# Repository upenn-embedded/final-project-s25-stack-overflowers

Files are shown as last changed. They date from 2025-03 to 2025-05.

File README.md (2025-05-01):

Review Assignment Due Date (https://classroom.github.com/a/WXeqVgks)

# final-project-skeleton

* Team Number: 14
* Team Name: Stack Overflowers
* Team Members: Sofia Hedlund and Amanda Tapia Garbelloto
* GitHub Repository URL: https://github.com/upenn-embedded/final-project-s25-stack-overflowers.git
* GitHub Pages Website URL: [for final submission]

## Final Project Proposal

### 1. Abstract

*In a few sentences, describe your final project.*

We want to make a braille printer that the user can input text into with a keyboard and have it print out the text into readable braille bumps. We plan to do this by 3D printing braille letters onto a stamp that will then rotated according to the text input and stamped down onto the paper with a motor. This project will use power management, interrupts for reading from the keyboard, and timers to control the stepper motor.

### 2. Motivation

*What is the problem that you are trying to solve? Why is this project interesting? What is the intended purpose?*

The project aims to enhance accessibility for people with reduced vision. By automatically transforming text into braille, people who can't see text are able to expand their integration to reading materials by possessing a personal device that can make any text available for them without requiring extra translators or specialized equipment.

### 3. System Block Diagram

*Show your high level design, as done in WS1 and WS2. What are the critical components in your system? How do they communicate (I2C?, interrupts, ADC, etc.)? What power regulation do you need?*
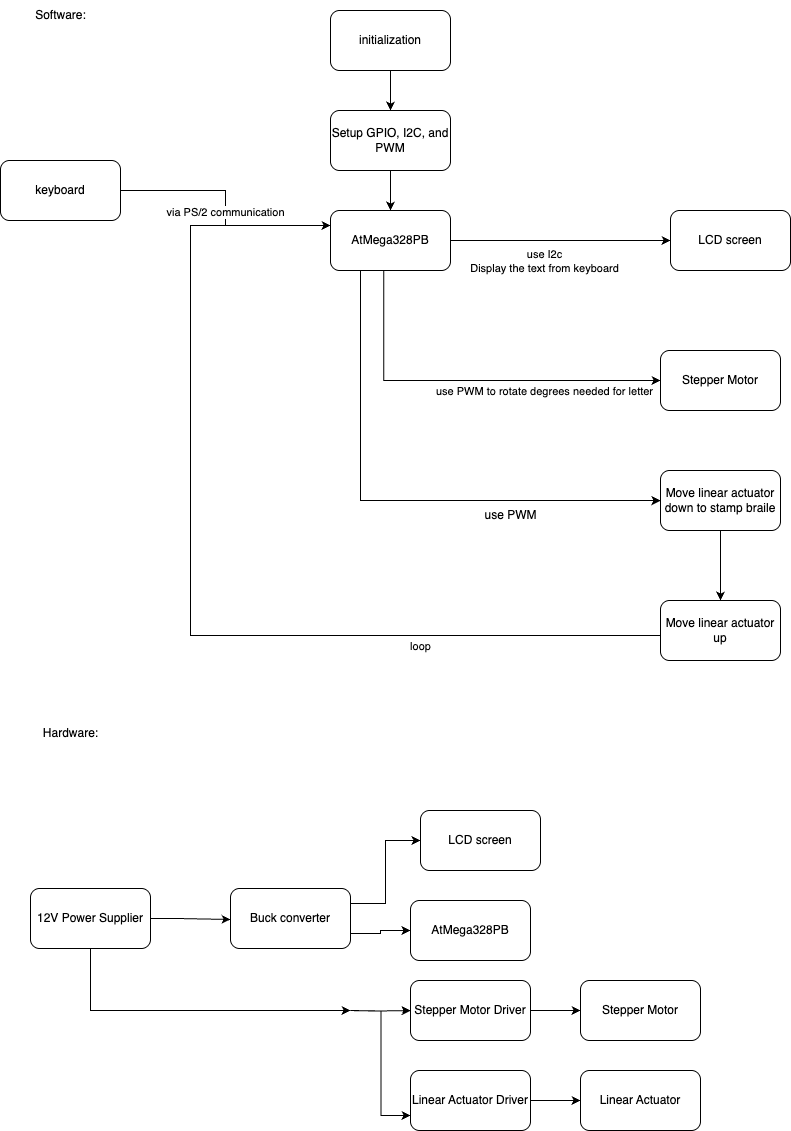
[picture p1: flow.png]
flow


### 4. Design Sketches

*What will your project look like? Do you have any critical design features? Will you need any special manufacturing techniques to achieve your vision, like power tools, laser cutting, or 3D printing?*
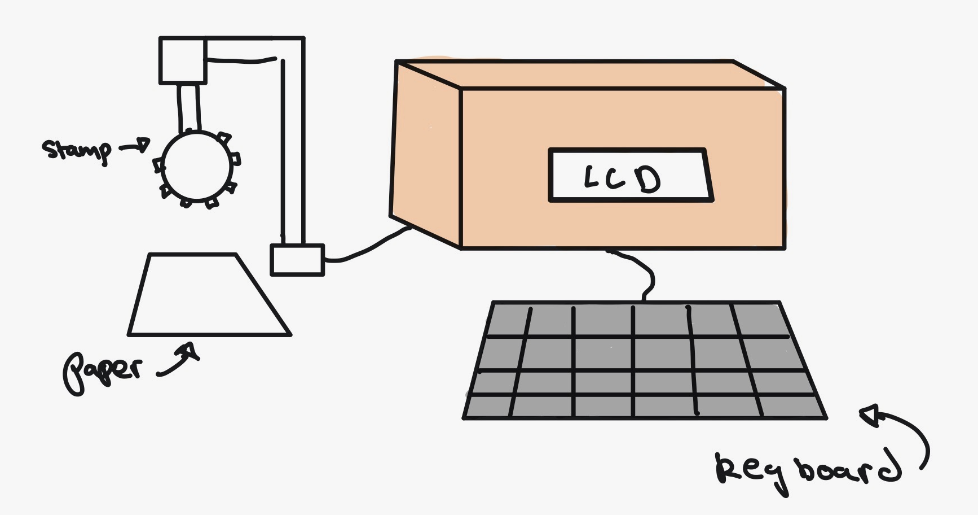
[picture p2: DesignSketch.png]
DesignSketch


We will need to 3D print the braille stamp to attach to the motor and also need some kind of container to hold the LCD and the wiring needed to power the system. We will also have to 3D print a stand to hold the linear actuator.

### 5. Software Requirements Specification (SRS)

*Formulate key software requirements here. Think deeply on the design: What must your device do? How will you measure this during validation testing? Create 4 to 8 critical system requirements.*

*These must be testable! See the Final Project Manual Appendix for details. Refer to the table below; replace these examples with your own.*

**5.1 Definitions, Abbreviations**

Here, you will define any special terms, acronyms, or abbreviations you plan to use for hardware

PWM- Pulse Width Modulation

ASCII- American Standard Code for Information Exchange

LCD- Liquid Crystal Display

**5.2 Functionality**

| ID     | Description                                                                                                                                                                                                                                                                               |
| ------ | ----------------------------------------------------------------------------------------------------------------------------------------------------------------------------------------------------------------------------------------------------------------------------------------- |
| SRS-01 | The microcontroller will process each letter of the text input and connect it to its corresponding braille. We can test its accuracy by plugging in sample characters and evaluating the different outputs of the MCU.                                                                    |
| SRS-02 | The system will translate each recognized letter into a PWM signals sending specific rotation angle for the Braille stamp mechanism, ensuring accurate letter selection. In this phase, we can actually measure the rotation angle for each character once we have our stamper connected. |
| SRS-03 | The stamping should be precisely timed, ensuring that the stepper motor finishes its rotation completely before the stamp is pressed again to prevent misalignment.                                                                                                                       |
| SRS-04 | The linear actuator will move the stamping mechanism, positioning the stamp at the correct location on the paper. The actuator should only move the stamp after it is pressed.                                                                                                            |
| SRS-05 | The software will have debouncing to filter out noise from the keyboard.                                                                                                                                                                                                                  |

### 6. Hardware Requirements Specification (HRS)

*Formulate key hardware requirements here. Think deeply on the design: What must your device do? How will you measure this during validation testing? Create 4 to 8 critical system requirements.*

*These must be testable! See the Final Project Manual Appendix for details. Refer to the table below; replace these examples with your own.*

**6.1 Definitions, Abbreviations**

Here, you will define any special terms, acronyms, or abbreviations you plan to use for hardware

Stepper Motor- DC motor that has very precise conotrol that will help us avoid error when rotating the stamp to the position of the letter.

Linear Actuator- Moves in a straight line so that we can move the stamp up and down.

**6.2 Functionality**

| ID     | Description                                                                                                                                                                                                                                                                       |
| ------ | --------------------------------------------------------------------------------------------------------------------------------------------------------------------------------------------------------------------------------------------------------------------------------- |
| HRS-01 | The device will require a keyboard module for text entry, this will communicate with the ATmega238 via PS/2.                                                                                                                                                                      |
| HRS-02 | It will also display the typed text to a LCD screen (I2C interface) to provide user feedback before printing. We will test the keyboard and the screen by seeing whether the later is displaying the correct keyboard inputs in real time.                                        |
| HRS-03 | The MCU will generate a PWM signal to control a stepper motor, which will rotate the Braille stamp mechanism to the correct character position. While working on this part we will ensure that the PWM signals are accurately rotating the stamp with a negligible error accuracy |
| HRS-04 | A linear actuator will move the stamp up and down to imprint the letters on to the paper A motor driver will be used to control the linear actuator, ensuring reliable movement without overloading the MCU.                                                                      |
| HRS-05 | The power system will need 12V power source and a buck converter for 5V to power the MCU, LCD, Stepper, and Linear Actuator.                                                                                                                                                      |

### 6. Bill of Materials (BOM)

*What major components do you need and why? Try to be as specific as possible. Your Hardware & Software Requirements Specifications should inform your component choices.*

*In addition to this written response, copy the Final Project BOM Google Sheet and fill it out with your critical components (think: processors, sensors, actuators). Include the link to your BOM in this section.*

The major components that we need are a stepper motor/driver to spin the braille stamp and a linear actuator/driver to move the stamp up and down. We chose our stepper motor in order have a lot precision over the amount of degrees the motor turns, so that the correct braille letter is stamped. We also chose for it to be 12V in order to ensure that it will have enough torque required to spin the braille stamp accurately. The driver will let us send simple STEP and DIR signals to control the stepper which will help us easily control the stepper. We chose a linear actuator to stamp down and a H-bridge so that we can move the actuator both up and down. Our budget was a main factor in choosing our linear actuator, because a lot of them were quite pricey (around 70$), so we chose the most affordable option we could find that fit with our system. We chose our keboard to be able to communicate over PS/2 because it is simpler to work with then USB communication which would likely need outside libraries. We will also use the LCD screen from Lab 4 and use the ATmega328Pb Xplained mini board.

[BOM](https://docs.google.com/spreadsheets/d/10AtQ8pPZeS8G-I5d4TY12WMqAhfvfrOR0J54DZgVhsI/edit?usp=sharing)

### 8. Final Demo Goals

*How will you demonstrate your device on demo day? Will it be strapped to a person, mounted on a bicycle, require outdoor space? Think of any physical, temporal, and other constraints that could affect your planning.*

We will demonstrate our device on demo day by entering in text to the keyboard, which will then be displayed on the LCD and then printed in braille by the stepper motor which will rotate to position the correct letter and the linear actuator which will stamp it down. Some physical constraints are that we need to have enough table space for the keyboard, LCD container, stepper motor, and paper. Because we are stamping the text out letter-by-letter, printing out a word or a short phrase will be more realistic to demonstrate out project without excessive time delay. At the end of the demo, the user can feel the braille stamped out on the paper, and can also compare it against the text on the LCD.

### 9. Sprint Planning

*You've got limited time to get this project done! How will you plan your sprint milestones? How will you distribute the work within your team? Review the schedule in the final project manual for exact dates.*

| Milestone  | Functionality Achieved                                                                                                                                    | Distribution of Work                                         |
| ---------- | --------------------------------------------------------------------------------------------------------------------------------------------------------- | ------------------------------------------------------------ |
| Sprint #1  | -3D print braille stamp<br />-Create rotating code for the stamp that maps characters to braille positions                                               | 3D printing- Amanda<br />Code- Sofia                         |
| Sprint #2  | -Add keyboard/LCD screen that displays the input text<br />-3D print stand for the linear actuator and stepper<br />-Debug rotation issues with the stamp | Keyboard/LCD- Sofia<br />3D print- Amanda <br />Debug- both |
| MVP Demo   | -Create code to move linear actuator up and down<br />-Debug movement with linear actuator                                                                | Code/movement- both                                          |
| Final Demo | -Refine precision of the motor movements                                                                                                                 | Both                                                         |

## Sprint Review #1

### Last week's progress

During this sprint, we finished the code to connect the serial terminal to the LCD screen so that it displays the text the user inputs. We also implemented the logic behind mapping the characters to their braille representations in binary, and the code to turn the pins the solenoids will be attached on to HIGH. We also started CAD for the structure that will hold the solenoids above the paper. We have committed the code for this part on github.

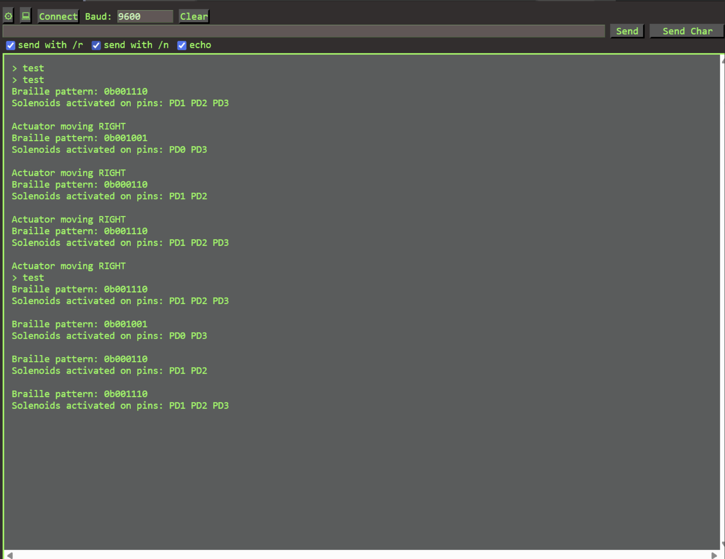
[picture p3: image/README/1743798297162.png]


### Current state of project

After the project presentation we got some feedback from the class on how to improve the stamping mechanism, so instead of using a wheel we will be working with six solenoids to support the full braille pattern.

We also took the professor's advice and are using our serial terminal to type out what we want to be translated to braille, instead of connecting another keyboard.

So, for each letter typed into the terminal, we have built the code that is recognizing them and translating it to the braille pattern, relating each dot to its correspondent solenoid and activating them. Since our parts have not arrived we still haven't tested their functionality, but so far our printed results seem to be in order. We have also wired the LCD screen and tested that it correctly displays what is being typed.

We have now ordered all the hardware parts needed for the project, but they haven't been delivered yet, so we are hoping to have them by next week so that we can also put them together with the stands we are designing and 3D printing. We have started working on the CAD structures for our supports and are planning on printing them this next week.

### Next week's plans

Next week we are going to be working on the hardware and testing the actual implementation of our code to the devices as soon as they arrive. So far we have the code for the solenoids push and pull, however since they were ordered later, we are probably going to implement first the movement of the linear actuator, which should follow the x-axis from right to left (since we are going to be stamping upside down).  Sofia will be working on combining the software and the hardware and debugging any issues that come up which will take around 5 hours, and will be considered “done” once the solenoids correctly move up and down with the character inputs and the linear actuator is able to move corresponding to each character.

We are also going to use the 3D printers to build the support for the solenoids and the box to keep most of our hardware connections, including the breadboards and ATmega238. Amanda will be working on 3D printing these supports with SolidWorks, which we are estimating will take around 5 hours and will be considered “done” once we send off the print request.

## Sprint Review #2

### Last week's progress

The solenoids that we ordered came, so we wired them with diodes and transistors and connected them to our MCU. From there, we debugged some issues with them correctly moving in and out, and realized two out of the six solenoids didn’t work properly, so we will be reordering them. We also completed and submitted CAD designs for a structure to hold the linear actuator and breadboard and also a structure to hold the actual solenoids.  We put the CAD files and a[ video](https://drive.google.com/file/d/1jELO6MgL8OEqHJt7nowW01g8Ehbm2qYE/view?usp=sharing) of the solenoids working with text input in the repo.

### Current state of project

At this point, we can see the braille patterns pretty accurately and have the LCD display our words at the same time as each letter is translated. We have wired part of the hardware and now need to add the linear actuator so that the motor moves on the x-axis as it prints on paper. We are waiting for the 3D printer to assemble all pieces and verify that they are the expected and can support our hardware accordingly.

### Next week's plan

Next week, we hope to figure out a way to attach a structure onto the tops of the solenoids so that when they move up and down they will stamp braille in the correct standardized dimensions. We also hope to get the linear actuator to work and move correctly as letters are stamped down. If the 3D print jobs are completed, we will also work on assembling the parts together.

We are planning on working together on most goals for next week, getting the linear actuator to work and debug any problems we might find with it should take around 4 hours to get the motor working and 3-5 hours for an attachment to the solenoids depending on how we implement it. Assembling the 3D pieces together should be pretty straightforward, but if we need to fix something or maybe redesign it, it might take up to 3 hours.

If everything works correctly, we also want to implement a feature connecting the braille machine to the blynk app, using the ESP32 interface so that we could try typing in our phones and getting the physical braille output.

## MVP Demo

1. Show a system block diagram & explain the hardware implementation.

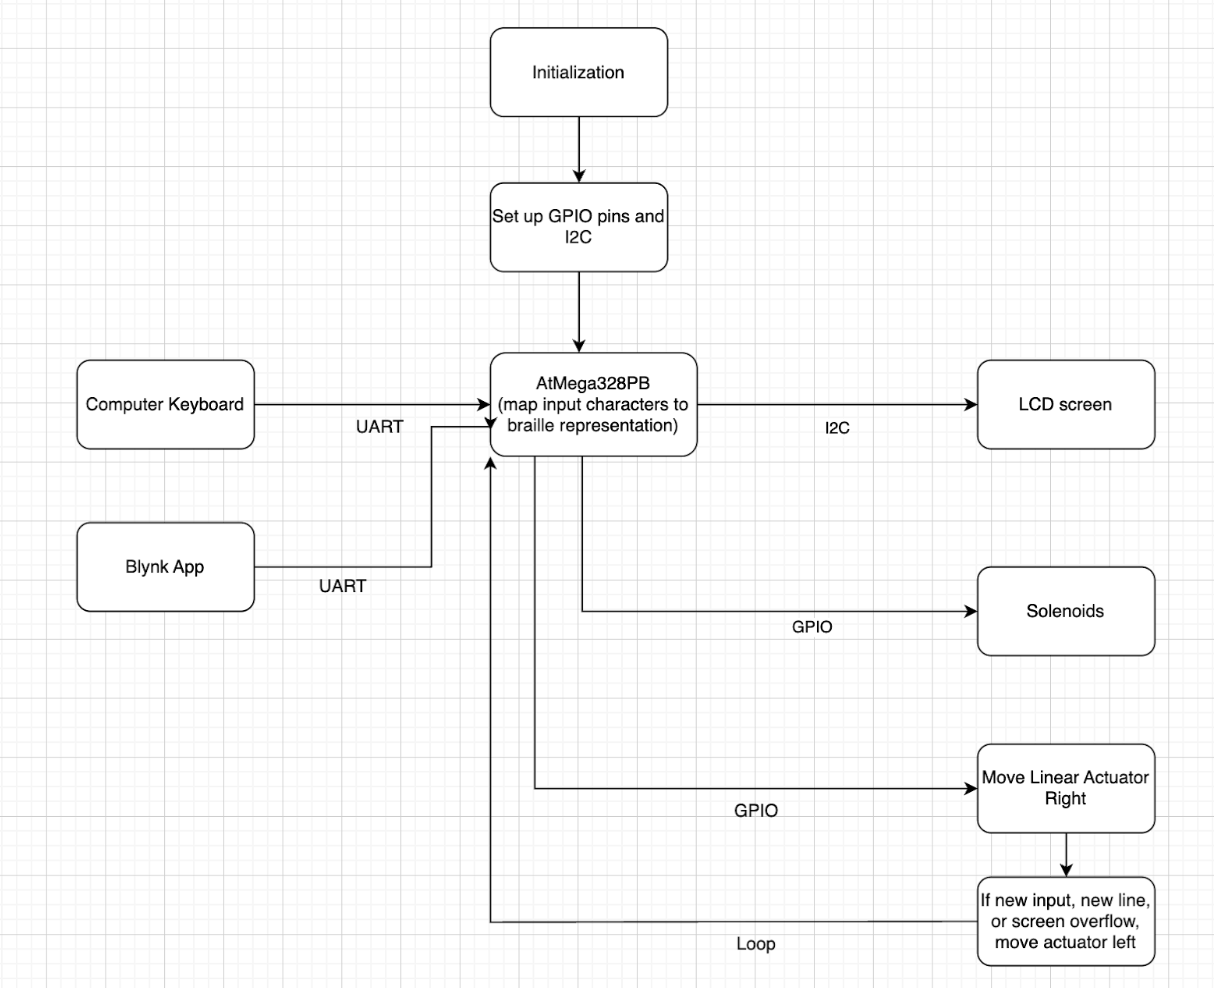
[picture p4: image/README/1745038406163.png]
   
2. Explain your firmware implementation, including application logic and critical drivers you've written.

   Our firmware currently takes in input using UART from the computer keyboard and converts it to bit representations of the Braille patterns. With these, it moves the solenoids up and down and the linear actuator right and left in order to create printed Braille. Using the UART driver, we store string inputs in a buffer and then process the string character-by-character by looking up the corresponding 6-bit Braille pattern from our table. In the bit representation, it will be a 1 if there is a bump and a 0 if there is no bump for each of the six Braille cells. These bits are then mapped to the six GPIO pins on our AtMega that control the solenoids in the activate_solenoids() function which sets and clears these pins with delays for stamping. We also have the functions actuator_move_out() and actuator_move_in() that control the GPIO pins to control the actuator for each character stamped out. The actuator moves out in between each character, and then will reset to the beginning of the line (moving in) for any new input, line overflow, or screen overflow. We also update an LCD screen in real-time as each character is stamped out so the user knows what is being written.
3. Demo your device.

   [https://drive.google.com/file/d/1WyQ7toSs-Gw57tEabU6b0ifRRfPq295w/view?usp=drivesdk](https://drive.google.com/file/d/1WyQ7toSs-Gw57tEabU6b0ifRRfPq295w/view?usp=drivesdk)

   [https://drive.google.com/file/d/1pV1rKBUoVU073-nwK2HYLF4Z8lEnAvDB/view?usp=drivesdk](https://drive.google.com/file/d/1pV1rKBUoVU073-nwK2HYLF4Z8lEnAvDB/view?usp=drivesdk)
4. Have you achieved some or all of your Software Requirements Specification (SRS)?

   1. Show how you collected data and the outcomes.
   2. We are using the LCD screen, which communicates over SPI, in order to display our typed inputs into the serial terminal. The screen shows our written words correctly and the linear actuator moves forth with each character and back at every new line to start typing the next input.
   3. Our motor and solenoids are also driven by GPIO. We changed our initial implementation, so we no longer needed to use PWM signals in order to rotate a stepper motor and instead are using GPIO to set the solenoids high or low according to our pattern.
   4. The timing precision of the machine has also been working reasonably well. We move the linear actuator after stamping each letter and then activate the solenoids. When a new input is written, representing a new line on the LCD, the actuator moves fully back and restart by the beginning of the line. We can still try to work on the precision of the movements, changing delays for example, but overall our system is working as expected.
5. Have you achieved some or all of your Hardware Requirements Specification (HRS)?

   1. Show how you collected data and the outcomes.
   2. We changed the interface of our input communicating tot he ATMega, so instead of a separate keyboard we are using the serial terminal connection (UART) from our laptops to the MCU and LCD display, which has been working accordinly.
   3. Our linear actuator and solenoids (stamping machine itself) are moving as expected. The linear actuator moves in the x-axis at every character and the solenoids are activated when it is no longer moving.
   4. We are using two different power sources. The Linear Actuator and the solenoids need 12V, so we ordered a battery to provide enough voltage and since the actuator also draws significant current (5A) we looked for a 12V battery with 7A current to support the actuator plus the six solenoids.
6. Show off the remaining elements that will make your project whole: mechanical casework, supporting graphical user interface (GUI), web portal, etc.

   We are still waiting to get our mechanical support for the linear actuator from the 3D printer. This element will be the overall case for the entire system and will provide a place to place the ATmega238 along with the breadboards. Internaly the box will also have a shelf to support the linear actuator, with a hole to the side were the moving part of our actuator will come out and move along the paper. This part of the linear actuator will also be propoerly connected to a solenoid support, where our six solenoids will be held in the right braille position and the bottom of each solenoid will be attached to a spike to poke the braille with correct pattern.

   In the firmware we will also finish implementing the connection between the feather and the serial terminal through UART so that we can use our phones to type our inputs. We will also work on debugging the current code and correcting any errors or delays which might be causing some unsynchronized movement between the solenoids and the actuator.

   We are still need to create a web portal for the project and add its link to our repo.
7. What is the riskiest part remaining of your project?

   The riskiest remaining part of our project is attaching parts to the tops of the solenoids so that we are able to print braille in the correct standard size/format. Because the solenoids are bulky currently, we need to design and apply attachments to each solenoid that will allow them to stamp in the braille with correct spacing to be readable.
   We also looked up the standard size of braille and are thinking of scaling it by 2 for making the stamp more visible and easier to manage due to our solenoid size and distance.

   1. How do you plan to de-risk this?

      We plan to de-risk this by properly trying out different materials that we can use to stamp down, such as 3D printing or rubber tips, and we will try attaching them in multiple ways to make sure that they are stable. We will also test out our braille stamp options on the braille paper, and adjust the stamping pressure with the solenoids depending on the results.
8. What questions or help do you need from the teaching team?

   We mostly need to continue debugging the motion of the linear actuator and finish assembling it with the 3D printed parts. We also hope to integrate it with the feather and the Blynk app which we could need some support with.

   From our last try, we were able get the inputs from the Blynk app to the serial terminal of the arduino, however, we still can't transmit the strings through UART to the LCD, so we will most likely go to office hours this week to finish this implementation.

## Final Project Report

Don't forget to make the GitHub pages public website!
If you’ve never made a GitHub pages website before, you can follow this webpage (though, substitute your final project repository for the GitHub username one in the quickstart guide):  [https://docs.github.com/en/pages/quickstart](https://docs.github.com/en/pages/quickstart)

### 1. Video

Here is a [link](https://drive.google.com/file/d/1xeawdyDZGxui-g1Ykbre4UoAcS7RQmn_/view?usp=sharing) to our final project! :)

### 2. Images

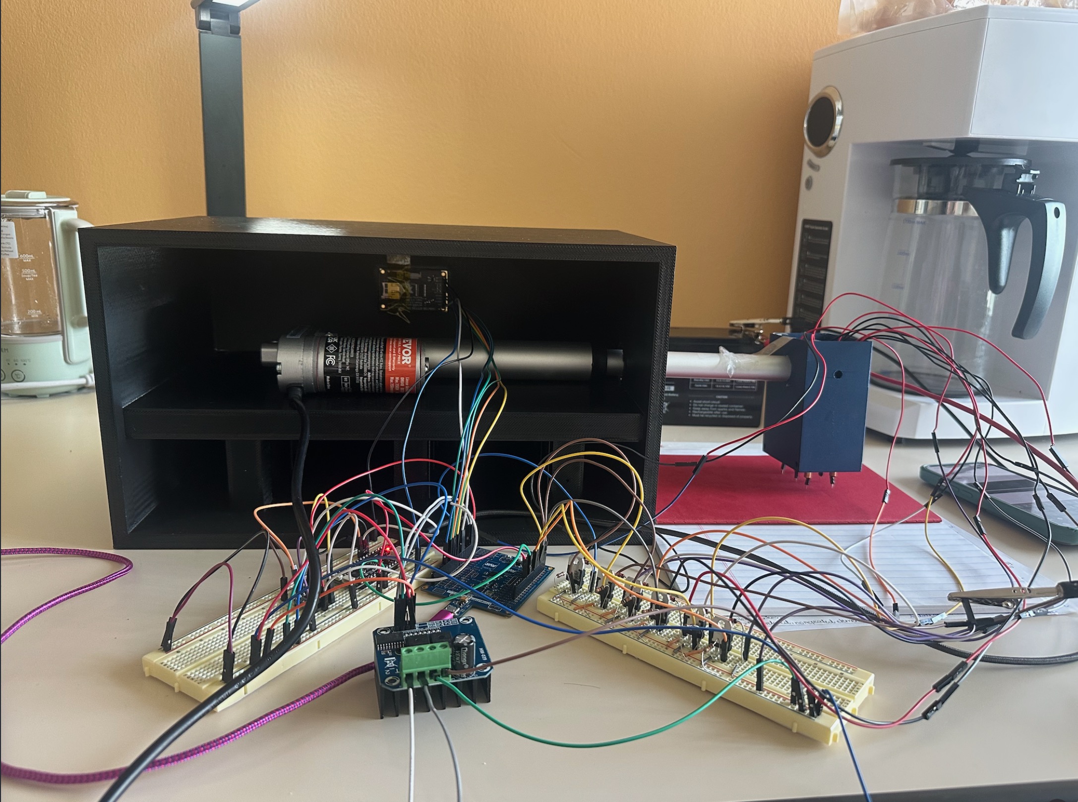
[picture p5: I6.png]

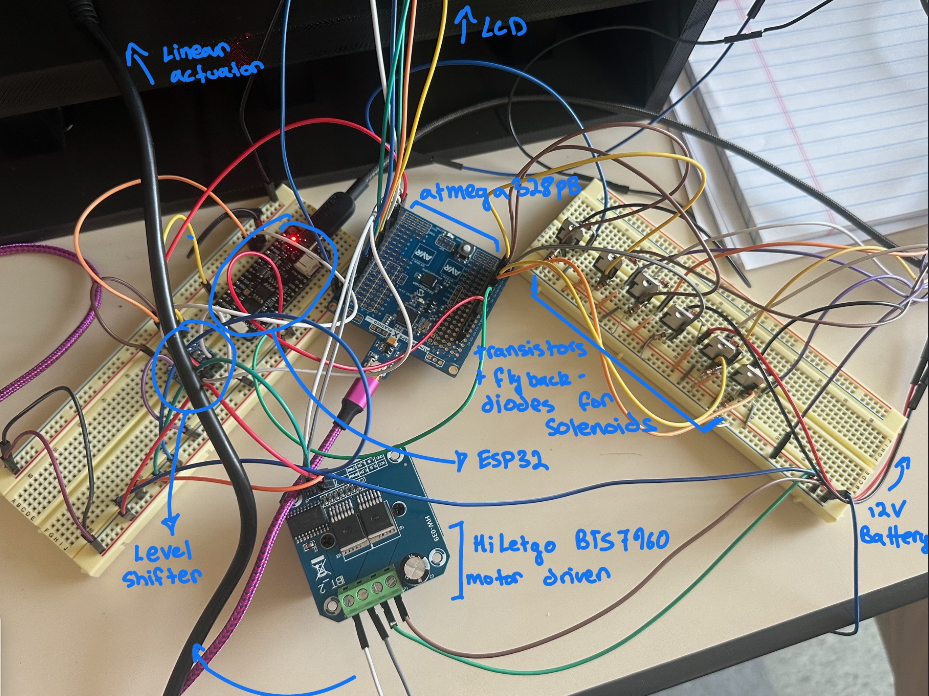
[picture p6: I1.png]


<p>
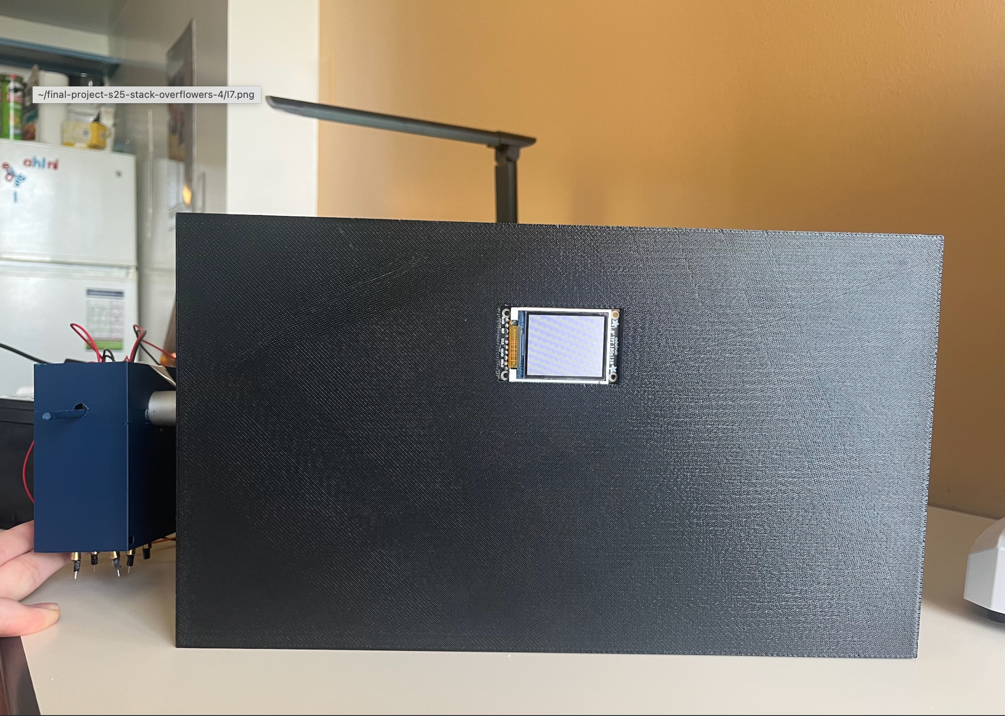
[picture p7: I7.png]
  
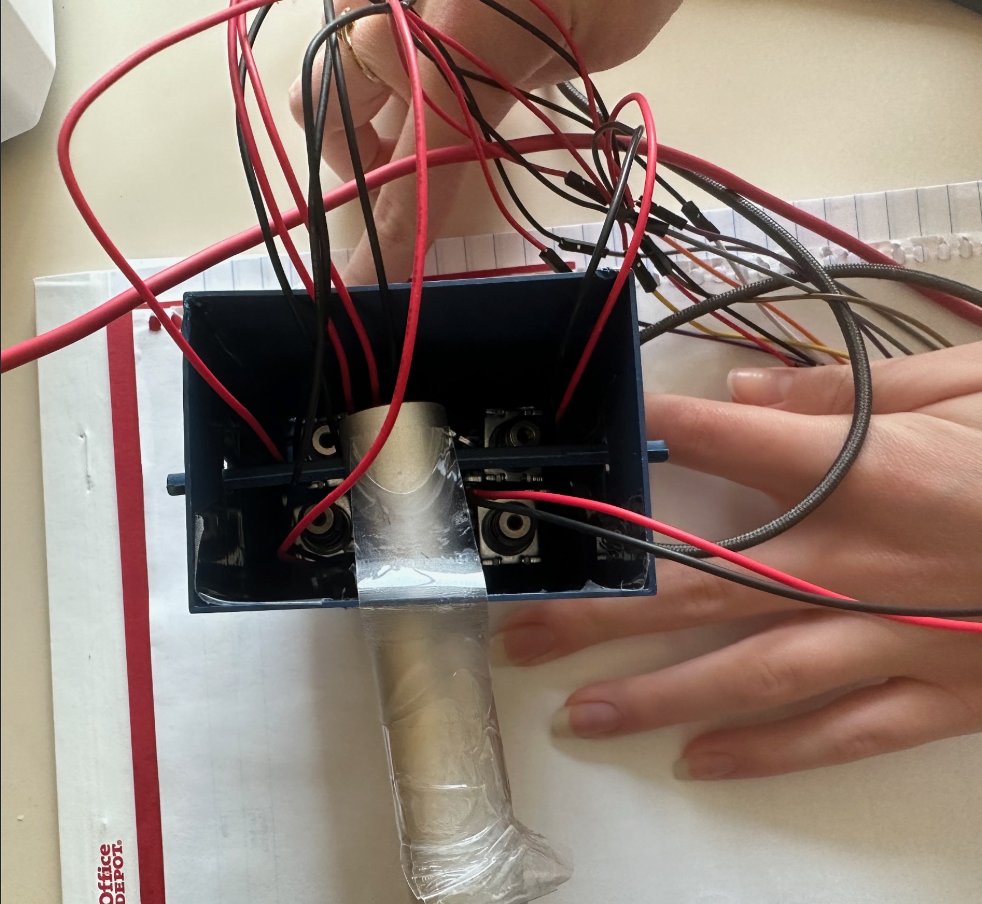
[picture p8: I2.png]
  
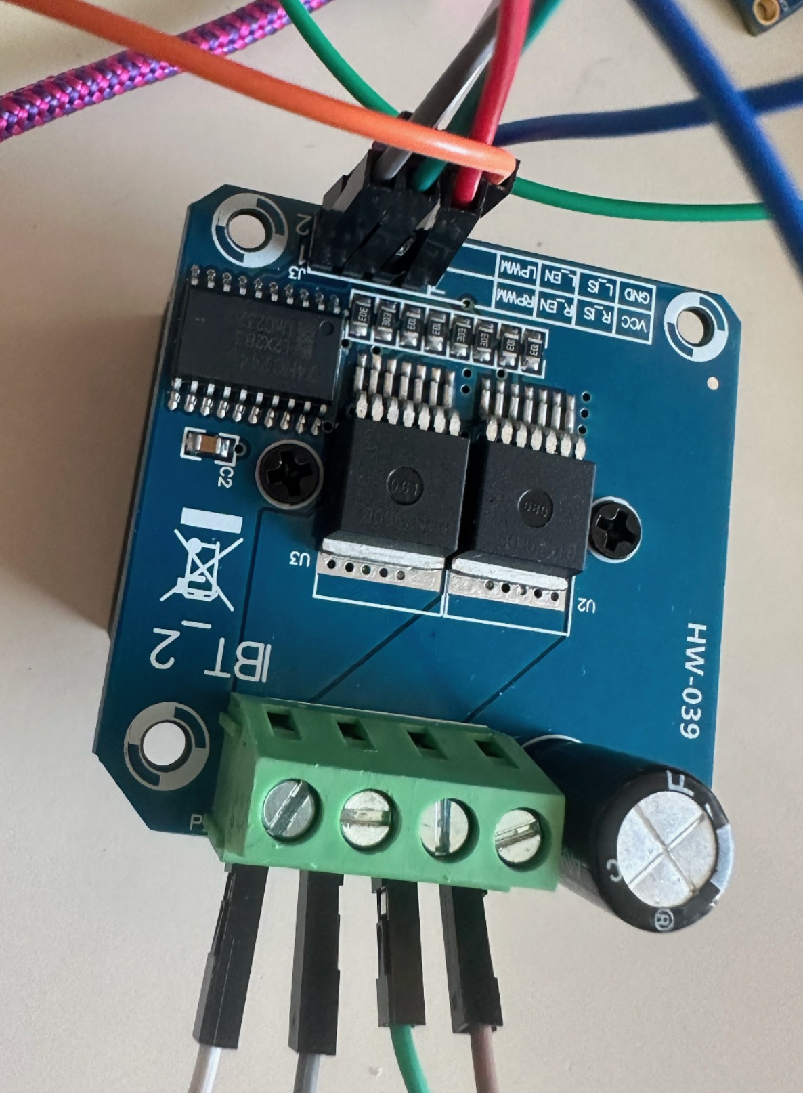
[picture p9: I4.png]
    
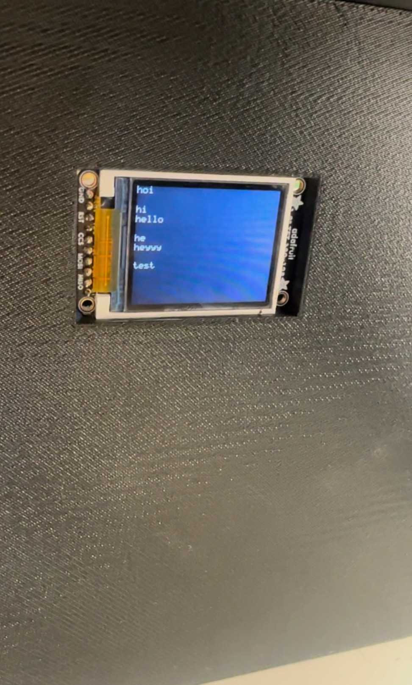
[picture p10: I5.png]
  
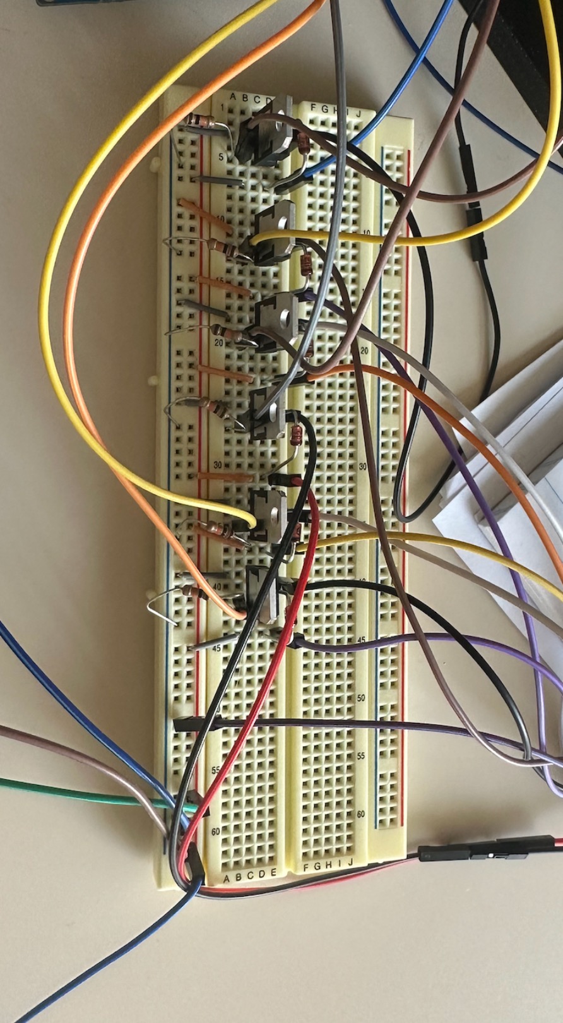
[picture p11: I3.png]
  
</p>

*Include photos of your device from a few angles. If you have a casework, show both the exterior and interior (where the good EE bits are!).*

### 3. Results

*What were your results? Namely, what was the final solution/design to your problem?*

Our proposal was to make braille printing more accessible and cheaper. From our final implementation we could design a stamping machine responsible for translating our typed inputs from our phones  sent through the  esp interface. We were able to build a reasonably functioning machine, which correctly related the inputs to the output pattern and activated solenoids responsible for stamping each respective character. Our linear actuator moves out after each letter is stamped and after a character count, when it reaches its maximum extended length, goes back in to restart and write on another line. We were able to implement both paths, having the actuator start untextended and move out, as well as having it move right to left (going from fully extended to its original length), which would be a more accurate representation of braille, since the stamping of the paper would happen upside down and required us to mirror all letters when accommodating the solenoids on their box.

We ran into a few problems when actually testing our stamp. We attached spike metals to the bottom of each solenoid (which proved pretty challenging),  so that they would poke the paper. But even  after we were able to have them fixed, the fact that we couldn't control the pressure of their stamps made it pretty hard to see what was being printed. We attempted using carbon paper to have a better result, but still couldn't make out the dot pattern in the paper, only a few scratches and dots. Another challenge was setting the solenoid box straight so that it wouldn't bend over one of the sides. Since our solenoid box was attached to the head of the linear actuator, it tilted on one side and this changed the direction of the stamps being activated, as well as the height at which we should position our paper. For these main hardware issues we weren't able to validate precisely our printed results on paper, but still had the software and electrical hardware working according to the expected, which should overall work for our primary purpose.

#### 3.1 Software Requirements Specification (SRS) Results

*Based on your quantified system performance, comment on how you achieved or fell short of your expected requirements.*

We could correctly program the firmware to recognize each character we put on the terminal and relate it to a specific braille pattern. We changed our implementation from using a rotation stamping moving up and down to a solenoid stamp, so we weren't required to implement PWM signals and used simply GPIO to control the activation of the solenoids and the linear actuator. In this case, instead of  measuring the precision of our design by having the right timing for the stepper and servo motor to move, we assured that our linear actuator started either fully extended or fully retracted at the beginning of each input and that it stopped when the solenoids were activated to stamp the paper and moved again after each character. We calculated the delay for separating each stamp and defined the maximum characters that would be in one line so that when that limit was reached the linear actuator would automatically go back to its initial placement.

For our serial communication requirement, we used SPI for the LCD screen, which displayed each character correctly as it was being stamped. We also implemented UART by connecting the ESP32 to the blynk app to capture the inputs out from our phone instead of only using only the serial terminal on our laptops.

*Did your requirements change? If so, why? Failing to meet a requirement is acceptable; understanding the reason why is critical!*

Even though we were only physically connected to PD0 with the ESP32, we found that sharing the USART0 interface between application data (from the ESP) and debug output (sent from the mcu to the terminal) caused interference. Our most logical explanation is that the bidirectional UART, as well as its buffers and timing must be synchronized in showing and receiving inputs and outputs. In this case when the ESP and the terminal tried to send signals and display the output from the mcu,  sharing a single USART resource, the serial communication broke down. Disconnecting the ESP from PD0 resolved the issue, and allowed us to receive the inputs from the laptop again, confirming that PD0 was being affected logically by the shared UART, not electrically. However, since our main goal was to be able to use the blynk interface, we chose to keep the wire plugged in and make full use of the ESP, disconnecting the serial terminal from our browser. We were also able to implement interrupts instead of pooling to capture the signals sent by UART to the mcu, however this implementation proved a bit tricky because we believe our debug statements to have interfered with the communication, in a way that although the hardware worked, we were not able to prove the accuracy of our results through the statements. Therefore we moved back to our previous approach and got to observe the response for every input sent

Some of our requirements did change from the moment we decided to take the approach of using solenoids instead of a rotating stamping machine, like changing from pwm to GPIO, and adapting the movement of the linear actuator to the x-axis. At the end, we also changed a bit of our logic, testing whether we should have the actuator fully extended or not at first and how much it should be extended even at its lowest point to fit our Solidworks design.

*Validate at least two requirements, showing how you tested and your proof of work (videos, images, logic analyzer/oscilloscope captures, etc.).*

| ID     | Description                                                                                                                                                                                                            | Validation Outcome                                                                                                                                                                                                                                                                                                                                                                                                      |
| ------ | ---------------------------------------------------------------------------------------------------------------------------------------------------------------------------------------------------------------------- | ----------------------------------------------------------------------------------------------------------------------------------------------------------------------------------------------------------------------------------------------------------------------------------------------------------------------------------------------------------------------------------------------------------------------- |
| SRS-01 | The microcontroller will process each letter of the text input and connect it to its corresponding braille. We can test its accuracy by plugging in sample characters and evaluating the different outputs of the mcu. | Confirmed with print statements sent to the terminal and by showing the activation of each solenoid. Image below where you can see the output of "overflower" is correctly mapped to the braille representation that is then actuated by the solenoids.                                                                                                                                                               |
| SRS-04 | The linear actuator will move the stamping mechanism, positioning the stamp at the correct location on the paper. The actuator should only move the stamp after it is pressed.                                         | Confirmed by the output. Here is a[link](https://drive.google.com/file/d/1pdvOI0gqZwETCkLKmU1SOwnsVDpanDDl/view?usp=sharing) to the linear actuator moving after each character. It only moves while the solenoids are not being activated. For a space, just the linear actuator moves and the solenoids do not fire. At the end of the input, the linear actuator moves all the way back in to the original position.  |

Image of SRS-01:

<p>
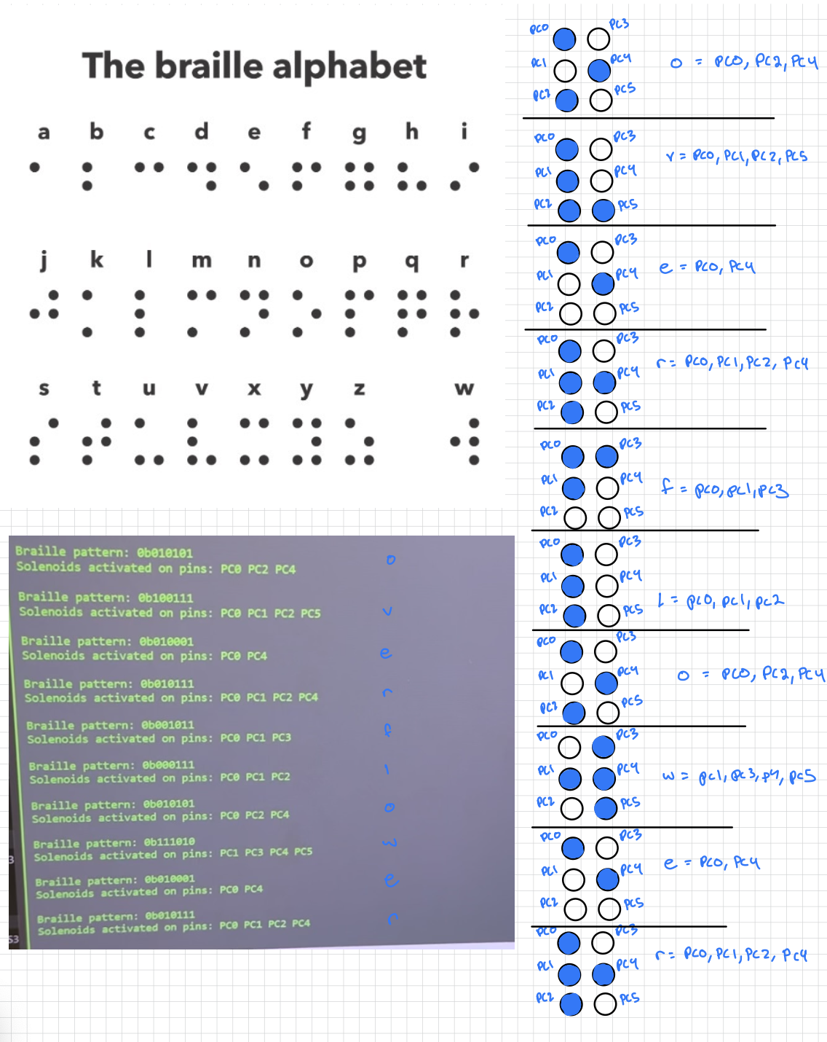
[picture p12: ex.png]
  
<p>

#### 3.2 Hardware Requirements Specification (HRS) Results

*Based on your quantified system performance, comment on how you achieved or fell short of your expected requirements.*

Overall we achieved most of our goals, having the printer process inputs as expected and our actuator and solenoids move accordingly. We encountered some difficulty in controlling the pressure that the solenoids would be pressed in the paper, making it somewhat difficult to see the stamping outcomes. We 3D printed our structure supporting the linear actuator and with enough space to also hold the breadboards and wires, as well as a smaller box holding the solenoids. Our bigger box had a space for our LCD screen, which correctly showed each character being stamped through SPI. The thickness of our box was bigger than we expected so when we changed our code so that the actuator never moved fully back in. Even when starting at the most retrieved position, the actuator was already slight extended making sure that the solenoid box was still properly attached to it, we recalculated the space it should move after each character and made sure that the actuator was only active after the solenoids were activated to ensure precise stamping.

*Did your requirements change? If so, why? Failing to meet a requirement is acceptable; understanding the reason why is critical!*

A few of our original ideas of implementation changed before we actually built the project. Following feedback from the professor, our first change was to use the serial terminal and UART communication from our own laptops as the inputs for the typed words.

Our initial idea also involved using a stepper motor to rotate a wheel machine which would move both horizontally and vertically to stamp each letter. From talking to our classmates we got feedback on how to simplify our mechanism using a set of six solenoids and our linear actuator to move horizontally on our paper and activate the precise solenoids to create the accurate letter. In this case, we were also able to work mainly with GPIO to activate the solenoids  instead of needing PWMs to rotate the wheel and could be more precise with the timing and spacing of the stamping.

On the practical side, we encountered a few issues in attaching a spike structure to the bottom of the solenoids and positioning them closer so that they would resemble a normal braille size. At the end, we were able to superglue pointy structures to the solensoids to punctuate the bottom of the paper, although the light pressure didn't allow us to see the correct pattern on paper.

We powered our 12V components through a battery but ended up not using a buck converter to step it down to 5V. Instead we used the ATmega output for 5V, but still had to shift down the voltage to 3.3 using the level shifter so that we could connect the ESP32. The device might also not be considered portable due to the size of the main box, however it would be perfectly plausible for each household with a visually disabled person to acquire and learn how to use one for a fairly cheap price.

*Validate at least two requirements, showing how you tested and your proof of work (videos, images, logic analyzer/oscilloscope captures, etc.).*

| ID     | Description                                                                                                                                                                                                                                                                                    | Validation Outcome                                                                                                                                                                                                                                                                                                                                                                                                                                       |
| ------ | ---------------------------------------------------------------------------------------------------------------------------------------------------------------------------------------------------------------------------------------------------------------------------------------------- | -------------------------------------------------------------------------------------------------------------------------------------------------------------------------------------------------------------------------------------------------------------------------------------------------------------------------------------------------------------------------------------------------------------------------------------------------------- |
| HRS-02 | It will also display the typed text to a LCD screen (I2C interface) to provide user feedback before printing. We will test the keyboard and the screen by seeing whether the later is displaying the correct keyboard inputs in real time.                                                     | Confirmed as observed in video. Each character appears on the screen simultaneously as its being printed. Here is a[link](https://drive.google.com/file/d/1S9dsCvcRlnqZN1PVkVOyjlvBThYYR3gt/view?usp=sharing) to the video.                                                                                                                                                                                                                                |
| HRS-04 | The motor will be mounted on a linear actuator, allowing it to move up and down (for stamping) and along the X-axis (for letter placement), working similarly to a plotter. A motor driverwill be used to control the linear actuator, ensuring reliable movement without overloading the MCU. | Partially confirmed. We used the linear actuator to move only in the x-direction, which worked precisely in timing and consistency with the motor driver. For the stamping up and down we used solenoids, connected and activated by the mcu and using diodes as a way to protect them from high voltages spikes as the motor turns off.  Here is a[link](https://drive.google.com/file/d/1oe5jddUY3IOjdkLFp_U5J3e_CTjTlkMo/view?usp=sharing) to the video. |

### 4. Conclusion

Reflect on your project. Some questions to address:

* What did you learn from it?
* What went well?
* What accomplishments are you proud of?
* What did you learn/gain from this experience?
* Did you have to change your approach?
* What could have been done differently?
* Did you encounter obstacles that you didn’t anticipate?
* What could be a next step for this project?

Our project went through many changes along the way, initially we thought of having a rotating stamp with alphabet characters and control two motors, a stepper motor through pwm to rotate the stamp and a servo motor through GPIO to move it up and down stamping the paper. By receiving feedback from the professor, the teaching team and our classmates we changed our implementation to receive the inputs directly from UART to the MCU and  created our braille pattern in solenoids which would automatically stamp the paper when activated, printing each letter.

This was one of our first times building an actual project from scratch and being responsible for all the design and implementation options. In the beginning, we were very cautious to understand what each component actually needed to do and how we would connect all elements both in hardware and software to reach our desired result. From software and hardware intersection in planning how to detect new inputs and activate our motors and solenoids precisely, to more hardware focused issues in finding an ideal battery for our 12V components and maximum current drawn, as well as building the structures to move our parts accordingly, and using solidworks to design the support for our components. We learned how to plan ahead and think of alternative solutions in case we forgot any small detail impacting our performance or had any pieces break or did not arrive in time.

Our final result was close to what we expected; we successfully implemented the UART for both our serial terminal and using the blynk application, which allowed us to type our inputs on our phones. We also were able to recognize each character and associate them to a pattern activating the solenoids through GPIO. And our actuator worked precisely after the stamps, leaving a standard space between each letter and going back to its original position at the start of each input, representing a new line. However, we encountered some problems with the actual stamp, while attaching structure to the bottom of the solenoids. Maybe a better solution would have been to print press fit structures and attach them to the solenoids, leading our spikes to the center of the solenoid holder so as to decrease the size of each character.

A next step for the project could be implementing another linear actuator responsible for moving in the y-direction, so that each new line would automatically start below the current one. In this case, we would have a real plotter stamping braille texts fully automatically. Another implementation would be scaling precisely the size of the characters by attaching structures to the bottom of the solenoids, centering the spiking stamps along the middle of the bottom of the solenoid box, making each stamp smaller and more realistic. In this case, the timing for extending the actuator would also change, so that the spacing between characters would be precisely scaled with their size. This would make the final machine more useful for actual applications by families or industries, being completely autonomous and standardized.

## References

LCD Library (Lab 4: Pong)

UART files from previous labs and ws.

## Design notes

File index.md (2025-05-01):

## Final Project Report

### 1. Video

Here is a [link](https://drive.google.com/file/d/1xeawdyDZGxui-g1Ykbre4UoAcS7RQmn_/view?usp=sharing) to our final project!! :)

### 2. Images

I6
I1

I7
I2
I4
I5
I3

### 3. Results

Our proposal was to make braille printing more accessible and cheaper. From our final implementation we could design a stamping machine responsible for translating our typed inputs from our phones sent through the ESP32 interface. We were able to build a functioning machine, which correctly related the inputs to the output pattern and activated solenoids responsible for stamping each respective character. Our linear actuator moves out after each letter is stamped and after a character count, when it reaches its maximum extended length, goes back in to restart and write on another line. We were able to implement both paths, having the actuator start unextended and move out, as well as having it move right to left (going from fully extended to its original length), which would be a more accurate representation of braille, since the stamping of the paper would happen upside down and required us to mirror all letters when accommodating the solenoids on their box.

We ran into a few problems when actually testing our stamp. We attached spike metals to the bottom of each solenoid, so that they would poke the paper. However, the light pressure of their stamps made it pretty hard to see what was being printed on paper. Therefore, we relied on print statements after every character to visualize the final output and compare the braille pattern we observed in the activated solenoids to their actual representation.

#### 3.1 Software Requirements Specification (SRS) Results

<br>

| ID     | Description                                                                                                                                                                                                                                                                              |
| ------ | ---------------------------------------------------------------------------------------------------------------------------------------------------------------------------------------------------------------------------------------------------------------------------------------- |
| SRS-01 | The microcontroller will process each letter of the text input and connect it to its corresponding braille. We can test its accuracy by plugging in sample characters and evaluating the different outputs of the MCU.                                                                   |
| SRS-02 | The system will translate each recognized letter into a PWM signal sending specific rotation angle for the Braille stamp mechanism, ensuring accurate letter selection. In this phase, we can actually measure the rotation angle for each character once we have our stamper connected. |
| SRS-03 | The stamping should be precisely timed, ensuring that the stepper motor finishes its rotation completely before the stamp is pressed again to prevent misalignment.                                                                                                                      |
| SRS-04 | The linear actuator will move the stamping mechanism, positioning the stamp at the correct location on the paper. The actuator should only move the stamp after it is pressed.                                                                                                           |
| SRS-05 | The software will have debouncing to filter out noise from the keyboard.                                                                                                                                                                                                                 |

<br>

We could correctly program the firmware to recognize each character we put on the terminal and relate it to a specific braille pattern. We changed our implementation from using a rotation stamping moving up and down to a solenoid stamp, so we weren't required to implement PWM signals and used simply GPIO to control the activation of the solenoids and the linear actuator. In this case, instead of measuring the precision of our design by having the right timing for the stepper and servo motor to move, we assured that our linear actuator started either fully extended or fully retracted at the beginning of each input and that it stopped when the solenoids were activated to stamp the paper and moved again after each character. We calculated the delay for separating each stamp and defined the maximum characters that would be in one line so that when that limit was reached the linear actuator would automatically go back to its initial placement.

For our serial communication requirement, we used SPI for the LCD screen, which displayed each character correctly as it was being stamped. We also implemented UART by connecting the ESP32 to the Blynk app to capture the inputs out from our phone instead of only using the serial terminal on our laptops.

Even though we were only physically connected to PD0 with the ESP32, we found that sharing the USART0 interface between application data (from the ESP) and debug output (sent from the MCU to the terminal) caused interference. Our most logical explanation is that the bidirectional UART, as well as its buffers and timing must be synchronized in showing and receiving inputs and outputs. In this case when the ESP and the terminal tried to send signals and display the output from the MCU, sharing a single USART resource, the serial communication broke down. Disconnecting the ESP from PD0 resolved the issue, and allowed us to receive the inputs from the laptop again, confirming that PD0 was being affected logically by the shared UART, not electrically. However, since our main goal was to be able to use the Blynk interface, we chose to keep the wire plugged in and make full use of the ESP, disconnecting the serial terminal from our browser. We were also able to implement interrupts instead of polling to capture the signals sent by UART to the MCU, however this implementation proved a bit tricky because we believe our debug statements interfered with the communication. Although the hardware worked, we were not able to prove the accuracy of our results through the statements. Therefore, we moved back to our previous approach and got to observe the response for every input sent.

Some of our requirements did change from the moment we decided to take the approach of using solenoids instead of a rotating stamping machine, like changing from PWM to GPIO, and adapting the movement of the linear actuator to the x-axis. At the end, we also changed a bit of our logic, testing whether we should have the actuator fully extended or not at first and how much it should be extended even at its lowest point to fit our SolidWorks design.

<br>

*Validating Requirements:*

<br>

| ID     | Description                                                                                                                                                                                                            | Validation Outcome                                                                                                                                                                                                                                                                                                                                                                                                   |
| ------ | ---------------------------------------------------------------------------------------------------------------------------------------------------------------------------------------------------------------------- | -------------------------------------------------------------------------------------------------------------------------------------------------------------------------------------------------------------------------------------------------------------------------------------------------------------------------------------------------------------------------------------------------------------------- |
| SRS-01 | The microcontroller will process each letter of the text input and connect it to its corresponding braille. We can test its accuracy by plugging in sample characters and evaluating the different outputs of the MCU. | Confirmed with print statements sent to the terminal and by showing the activation of each solenoid. Image below where you can see the output of "overflower" is correctly mapped to the braille representation that is then actuated by the solenoids.                                                                                                                                                              |
| SRS-04 | The linear actuator will move the stamping mechanism, positioning the stamp at the correct location on the paper. The actuator should only move the stamp after it is pressed.                                         | Confirmed by the output. Here is a[link](https://drive.google.com/file/d/1pdvOI0gqZwETCkLKmU1SOwnsVDpanDDl/view?usp=sharing) to the linear actuator moving after each character. It only moves while the solenoids are not being activated. For a space, just the linear actuator moves and the solenoids do not fire. At the end of the input, the linear actuator moves all the way back in to the original position. |

Stamping Output

#### 3.2 Hardware Requirements Specification (HRS) Results

<br>

| ID     | Description                                                                                                                                                                                                                                                                        |
| ------ | ---------------------------------------------------------------------------------------------------------------------------------------------------------------------------------------------------------------------------------------------------------------------------------- |
| HRS-01 | The device will require a keyboard module for text entry, this will communicate with the ATmega238 via PS/2.                                                                                                                                                                       |
| HRS-02 | It will also display the typed text to a LCD screen (I2C interface) to provide user feedback before printing. We will test the keyboard and the screen by seeing whether the latter is displaying the correct keyboard inputs in real time.                                        |
| HRS-03 | The MCU will generate a PWM signal to control a stepper motor, which will rotate the Braille stamp mechanism to the correct character position. While working on this part we will ensure that the PWM signals are accurately rotating the stamp with a negligible error accuracy. |
| HRS-04 | A linear actuator will move the stamp up and down to imprint the letters onto the paper. A motor driver will be used to control the linear actuator, ensuring reliable movement without overloading the MCU.                                                                       |

<br>

*Validating Requirements:*

<br>

| ID     | Description                                                                                                                                                                                                                                                                                     | Validation Outcome                                                                                                                                                                                                                                                                                                                                                                                                                                     |
| ------ | ----------------------------------------------------------------------------------------------------------------------------------------------------------------------------------------------------------------------------------------------------------------------------------------------- | ------------------------------------------------------------------------------------------------------------------------------------------------------------------------------------------------------------------------------------------------------------------------------------------------------------------------------------------------------------------------------------------------------------------------------------------------------ |
| HRS-02 | It will also display the typed text to a LCD screen (I2C interface) to provide user feedback before printing. We will test the keyboard and the screen by seeing whether the latter is displaying the correct keyboard inputs in real time.                                                     | Confirmed as observed in video. Each character appears on the screen simultaneously as it’s being printed. Here is a[link](https://drive.google.com/file/d/1S9dsCvcRlnqZN1PVkVOyjlvBThYYR3gt/view?usp=sharing) to the video.                                                                                                                                                                                                                             |
| HRS-04 | The motor will be mounted on a linear actuator, allowing it to move up and down (for stamping) and along the X-axis (for letter placement), working similarly to a plotter. A motor driver will be used to control the linear actuator, ensuring reliable movement without overloading the MCU. | Partially confirmed. We used the linear actuator to move only in the x-direction, which worked precisely in timing and consistency with the motor driver. For the stamping up and down we used solenoids, connected and activated by the MCU and using diodes as a way to protect them from high voltage spikes as the motor turns off. Here is a[link](https://drive.google.com/file/d/1oe5jddUY3IOjdkLFp_U5J3e_CTjTlkMo/view?usp=sharing) to the video. |

### 4. Conclusion

Our project went through many changes along the way. Initially, we thought of having a rotating stamp with alphabet characters and controlling two motors — a stepper motor through PWM to rotate the stamp and a servo motor through GPIO to move it up and down to stamp the paper. By receiving feedback from the professor, the teaching team, and our classmates, we changed our implementation to receive the inputs directly from UART to the MCU and created our braille pattern in solenoids which would automatically stamp the paper when activated, printing each letter.

This was one of our first times building an actual project from scratch and being responsible for all the design and implementation options. In the beginning, we were very cautious to understand what each component actually needed to do and how we would connect all elements both in hardware and software to reach our desired result. From software and hardware intersection in planning how to detect new inputs and activate our motors and solenoids precisely, to more hardware-focused issues in finding an ideal battery for our 12V components and maximum current drawn, as well as building the structures to move our parts accordingly, and using SolidWorks to design the support for our components. We learned how to plan ahead and think of alternative solutions in case we forgot any small detail impacting our performance or had any pieces break or did not arrive in time.

Our final result was close to what we expected; we successfully implemented UART for both our serial terminal and the Blynk application, which allowed us to type our inputs on our phones. We also were able to recognize each character and associate them to a pattern activating the solenoids through GPIO. And our actuator worked precisely after the stamps, leaving a standard space between each letter and going back to its original position at the start of each input, representing a new line. However, we encountered some problems with the actual stamp, while attaching structure to the bottom of the solenoids. Maybe a better solution would have been to print press-fit structures and attach them to the solenoids, leading our spikes to the center of the solenoid holder so as to decrease the size of each character.

A next step for the project could be implementing another linear actuator responsible for moving in the y-direction, so that each new line would automatically start below the current one. In this case, we would have a real plotter stamping braille texts fully automatically. Another implementation would be scaling precisely the size of the characters by attaching structures to the bottom of the solenoids, centering the spiking stamps along the middle of the bottom of the solenoid box, making each stamp smaller and more realistic. In this case, the timing for extending the actuator would also change, so that the spacing between characters would be precisely scaled with their size. This would make the final machine more useful for actual applications by families or industries, being completely autonomous and standardized.

## References

LCD Library (Lab 4: Pong)

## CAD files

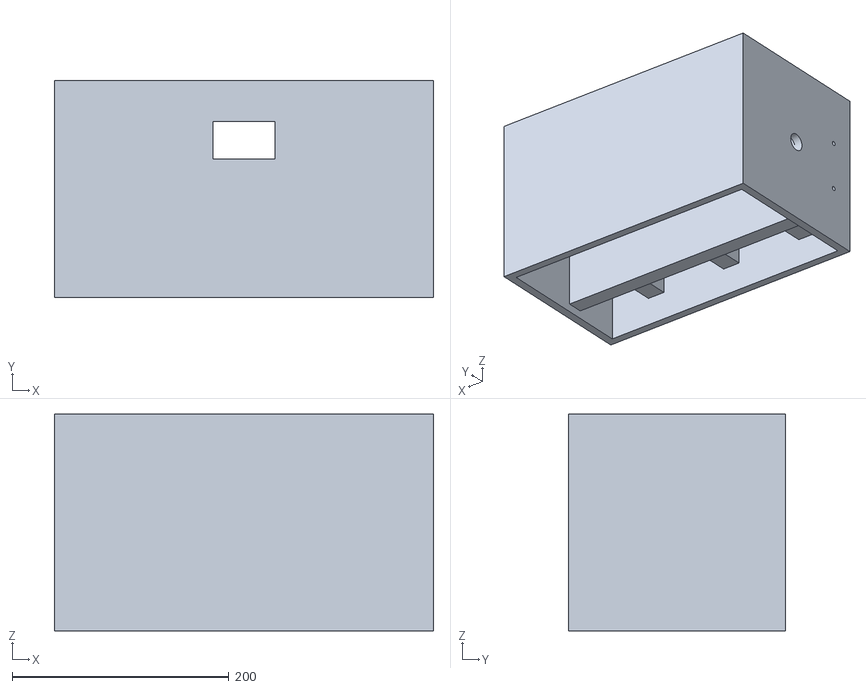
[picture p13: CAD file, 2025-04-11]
LCD Box.STL
350.0 x 200.0 x 200.0

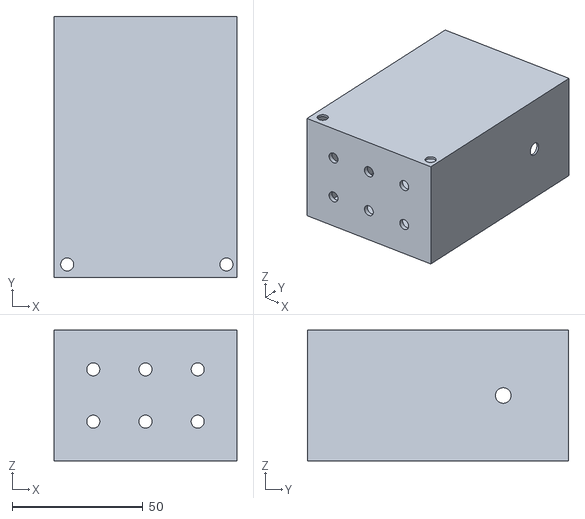
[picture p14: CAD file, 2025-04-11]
Solenoid Holder.STL
70.0 x 100.0 x 50.0

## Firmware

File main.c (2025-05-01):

#define F_CPU 16000000UL

 #include <avr/io.h>
 #include "lib\ST7735.h"
 #include "lib\LCD_GFX.h"
 #include <util/delay.h>
 #include <stdio.h>
 #include <stdlib.h>
 #include <time.h>
 #include "uart.h"
#include <avr/interrupt.h>

#define DOT1_PIN PC0
#define DOT2_PIN PC1
#define DOT3_PIN PC2
#define DOT4_PIN PC3
#define DOT5_PIN PC4
#define DOT6_PIN PC5
#define SOLENOID_PORT PORTC
#define SOLENOID_DDR  DDRC
#define MAX_LINE_LENGTH 64
char buffer[MAX_LINE_LENGTH];
volatile int buffer_index = 0;
volatile uint8_t line_ready = 0;

#define ACTUATOR_UP_PIN   PD2
#define ACTUATOR_DOWN_PIN PD3

#define ACTUATOR_PORT PORTD
#define ACTUATOR_DDR  DDRD
#define BUFFER_COUNT 2

void actuator_move_out() {
    ACTUATOR_PORT &= ~(1 << ACTUATOR_DOWN_PIN);   // right LOW
    ACTUATOR_PORT |= (1 << ACTUATOR_UP_PIN);      // left HIGH
    printf("Actuator moving OUT\n");
    //corresponds to the correct spacing of 12mm in between braille characters
    //for double-size braille
    _delay_ms(2400);
    ACTUATOR_PORT &= ~(1 << ACTUATOR_UP_PIN);     // stop
}

void actuator_move_in() {
    ACTUATOR_PORT &= ~(1 << ACTUATOR_UP_PIN);     // left LOW
    ACTUATOR_PORT |= (1 << ACTUATOR_DOWN_PIN);    // right HIGH
    printf("Actuator moving IN\n");
    //time to make it go all the way back in fromm full extension
    _delay_ms(2400);
    ACTUATOR_PORT &= ~(1 << ACTUATOR_DOWN_PIN);   // stop
}

void actuator_fully_extend() {
    ACTUATOR_PORT &= ~(1 << ACTUATOR_DOWN_PIN);   // right LOW
    ACTUATOR_PORT |= (1 << ACTUATOR_UP_PIN);      // left HIGH
    printf("Fully extending actuator\n");
    // Longer time to ensure full extension
    _delay_ms(15000);
    ACTUATOR_PORT &= ~(1 << ACTUATOR_UP_PIN);     // stop
}


void activate_solenoids(uint8_t pattern) {
    // clear solenoids
    SOLENOID_PORT &= ~0b00111111;
    // set the solenoids based on braille map
    SOLENOID_PORT |= (pattern & 0b00111111);

    _delay_ms(1000);  // delay to stamp down
    SOLENOID_PORT &= ~0b00111111;//clear solenoids again
   
//    testing without hardware:
    printf("Braille pattern: 0b");
    for (int i = 5; i >= 0; i--) {
        printf("%d", (pattern >> i) & 1); // print each bit from dot6 to dot1
    }
    printf("\n");
    printf("Solenoids activated on pins: ");
    for (int i = 0; i < 6; i++) {
        if ((pattern >> i) & 1) {
            printf("PC%d ", i);
        }
    }
    printf("\n\n");
   
    _delay_ms(300); // time to press
    SOLENOID_PORT &= ~0b00111111;
}

// 6 bits: dot1 is LSB, dot6 is MSB
typedef struct {
    char ascii;
    uint8_t braille_pattern;
} BrailleMap;

BrailleMap braille_table[] = {
    {'a', 0b000001},
    {'b', 0b000011},
    {'c', 0b001001},
    {'d', 0b011001},
    {'e', 0b010001},
    {'f', 0b001011},
    {'g', 0b011011},
    {'h', 0b010011},
    {'i', 0b001010},
    {'j', 0b011010},
    {'k', 0b000101},
    {'l', 0b000111},
    {'m', 0b001101},
    {'n', 0b011101},
    {'o', 0b010101},
    {'p', 0b001111},
    {'q', 0b011111},
    {'r', 0b010111},
    {'s', 0b001110},
    {'t', 0b011110},
    {'u', 0b100101},
    {'v', 0b100111},
    {'w', 0b111010},
    {'x', 0b110011},
    {'y', 0b111101},
    {'z', 0b110101}
};

uint8_t get_braille_pattern(char input) {
    //go through every element in braille table
    for (int i = 0; i < sizeof(braille_table)/sizeof(BrailleMap); i++) {
        //check if ascii field is char of input
        if (braille_table[i].ascii == input) {
            //return the bit value of the braille
            return braille_table[i].braille_pattern;
        }
    }
    return 0;
}

int main(void) {
    uart_init();      
    lcd_init();      
    LCD_setScreen(BLACK);
   
    // set solenoid pins (PD0 through PD5) as output
    SOLENOID_DDR |= 0b00111111;
   
    //setup actuator
    ACTUATOR_DDR |= (1 << ACTUATOR_UP_PIN) | (1 << ACTUATOR_DOWN_PIN);
    int cursor_x = 0;
    int cursor_y = 0;
   
    actuator_fully_extend();


    while (1) {
        if (uart_available()) {
        char c = uart_receive(NULL);
//        printf("Got: %c\n", c);

        if (c == '\r' || c == '\n') {
            buffer[buffer_index] = '\0'; // end
            int char_count = 0;

            // print the whole string now
            //for each character in buffer print it out and move cursor forward
            for (int i = 0; i < buffer_index; i++) {
               
                LCD_drawChar(cursor_x, cursor_y, buffer[i], WHITE, BLACK);
                cursor_x += 6;
               
                //get braille pattern
                uint8_t pattern = get_braille_pattern(buffer[i]);
                activate_solenoids(pattern);
               
                actuator_move_in();//
                char_count++;
               
                //maximum extension of the linear actuator
                //moves it back in to start a new line after 14 char
                if (char_count == 14) {
                actuator_move_out();//changed from move in
                char_count = 0;
                }
               
                //go to next line if overflow
                if (cursor_x >= LCD_WIDTH - 6) {
                    cursor_x = 0;
                    cursor_y += 10;
                   
//                    actuator_move_in();
                   
                }
               
                //go to new screen if overflow
                if (cursor_y >= LCD_HEIGHT - 10) {
                    LCD_setScreen(BLACK);
                    cursor_x = 0;
                    cursor_y = 0;
                   
                    actuator_move_out(); //changed from move in
                   
                }
            }
            //start new input on new line
            actuator_move_out(); //changed from move in
            cursor_y += 10;
            cursor_x = 0;

            // reset buffer
            buffer_index = 0;
           
            } else {
                if (buffer_index < MAX_LINE_LENGTH - 1) {
                    buffer[buffer_index++] = c;
                }
            }
        }
        _delay_ms(1);
    }
}

////test just the linear actuator
//int main(void) {
//    // Set PD2 and PD3 as output
//    ACTUATOR_DDR |= (1 << ACTUATOR_UP_PIN) | (1 << ACTUATOR_DOWN_PIN);
//    uart_init();
//
//    while (1) {
//      actuator_move_out();
//       _delay_ms(2000); // Wait 2 seconds
//    }
//}

//
//// double buffers
//volatile struct {
//    char data[BUFFER_COUNT][MAX_LINE_LENGTH];
//    volatile uint8_t write_index;    //buffer being written to
//    volatile uint8_t read_index;     // buffer to be read
//    volatile uint8_t position;       //pos in writing buffer
//    volatile uint8_t buffer_ready;   // flag to show a buffer is ready to read
//    volatile uint8_t buffer_full;    // Flag to show curr write buffer is full
//} uart_buffer = {
//    .write_index = 0,
//    .read_index = 1,
//    .position = 0,
//    .buffer_ready = 0,
//    .buffer_full = 0
//};
//
//ISR(USART0_RX_vect) {
//    // read the received character
//    char c = UDR0;
//    
//    // check error flags
//    uint8_t status = UCSR0A;
//    if (status & ((1 << FE0) | (1 << DOR0) | (1 << UPE0))) {
//        // clear error
//        return;
//    }
//    
//    // debug message
//    static uint8_t debug_counter = 0;
//    
//    // add to buffer
//    if (uart_buffer.position < MAX_LINE_LENGTH - 1) {
//        uart_buffer.data[uart_buffer.write_index][uart_buffer.position++] = c;
//        if (c == '\r' || c == '\n') {
//            // add null terminate
//            uart_buffer.data[uart_buffer.write_index][uart_buffer.position-1] = '\0';
//            
//            // mark as ready
//            uart_buffer.buffer_ready = 1;
//
//            uint8_t temp = uart_buffer.write_index;
//            uart_buffer.write_index = uart_buffer.read_index;
//            uart_buffer.read_index = temp;
//            uart_buffer.position = 0;
//        }
//    }
//    debug_counter++;
//}
//
//// check if line is available
//uint8_t uart_line_available(void) {
//    return uart_buffer.buffer_ready;
//}
//
//// function to get line
//char* uart_get_line(void) {
//    if (uart_buffer.buffer_ready) {
//        return (char*)uart_buffer.data[uart_buffer.read_index];
//    }
//    return NULL;
//}
//
//void uart_line_processed(void) {
//    uart_buffer.buffer_ready = 0;
//}
//
//int main(void) {
//    // initialize
//    uart_init();
//    lcd_init();
//    LCD_setScreen(BLACK);
//    
//    // set solenoids
//    SOLENOID_DDR |= 0b00111111;
//    
//    // setup actuator pins
//    ACTUATOR_DDR |= (1 << ACTUATOR_UP_PIN) | (1 << ACTUATOR_DOWN_PIN);
//    
//    LCD_drawString(0, 0, "uart ready", WHITE, BLACK);
//    
//    // enable interrupts
//    sei();
//    
//    //test
//    printf("uart test\r\n");
//    
//    int cursor_x = 0;
//    int cursor_y = 20;
//    
//    actuator_fully_extend();
//
//    while (1) {
//        // check if available
//        if (uart_line_available()) {
//            // Get the line
//            char* current_line = uart_get_line();
//            
//            // update
//            LCD_drawString(0, 10, "processing", WHITE, BLACK);
//            
//            actuator_fully_extend();
//            int char_count = 0;
//            
//            // process characters in line
//            for (int i = 0; current_line[i] != '\0'; i++) {
//                // display
//                LCD_drawChar(cursor_x, cursor_y, current_line[i], WHITE, BLACK);
//                cursor_x += 6;
//                
//                // map solenoids
//                uint8_t pattern = get_braille_pattern(current_line[i]);
//                activate_solenoids(pattern);
//
//                actuator_move_in();
//                char_count++;
//                
//                if (char_count == 14) {
//                    actuator_move_out();
//                    char_count = 0;
//                }
//                
//                if (cursor_x >= LCD_WIDTH - 6) {
//                    cursor_x = 0;
//                    cursor_y += 10;
//                }
//                
//                if (cursor_y >= LCD_HEIGHT - 10) {
//                    LCD_setScreen(BLACK);
//                    LCD_drawString(0, 0, "uart is ready", WHITE, BLACK);
//                    cursor_x = 0;
//                    cursor_y = 20;
//                    actuator_move_out();
//                }
//            }
//            
//            //mark as processed
//            uart_line_processed();
//            
//            // get ready for next input
//            actuator_move_out();
//            cursor_y += 10;
//            cursor_x = 0;
//            
//            LCD_drawString(0, 10, "ready for next line", WHITE, BLACK);
//        }
//        
//        _delay_ms(10);
//    }
//}
//
//

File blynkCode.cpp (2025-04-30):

/* Comment this out to disable prints and save space */
#define BLYNK_PRINT Serial

/* Fill-in your Template ID (only if using Blynk.Cloud) */
#define BLYNK_TEMPLATE_ID           "TMPL2AbcmmxM2"
#define BLYNK_TEMPLATE_NAME         "ESE3500"
#define BLYNK_AUTH_TOKEN            "GbFkys4_FPw8G8-EQ9veBrG9TAoxZ7Q4"

// Your WiFi credentials.
// Set password to "" for open networks.
#define MY_SSID                     "AirPennNet-Device"
#define MY_PASSWORD                 "penn1740wifi"

#include <WiFi.h>
#include <WiFiClient.h>
#include <BlynkSimpleEsp32.h>

// You should get Auth Token in the Blynk App.
// Go to the Project Settings (nut icon).
char auth[] = BLYNK_AUTH_TOKEN;

// Define UART pins for communication with ATMEGA
#define UART_TX_PIN 17
#define UART_RX_PIN 18  

void setup()
{
  // Debug console to USB serial
  Serial.begin(115200);
  
  // UART communication with ATMEGA
  Serial1.begin(9600, SERIAL_8N1, UART_RX_PIN, UART_TX_PIN);
  
  // Connect to Blynk
  Blynk.begin(auth, MY_SSID, MY_PASSWORD);
  
  Serial.println("ESP32 initialized and connected to Blynk");
}

{
  Blynk.run();
  
  // Forward serial data from ATMEGA to debug console
  while (Serial1.available()) {
    char c = Serial1.read();
    Serial.write(c);  
  }
}

BLYNK_WRITE(V0)
{
  String inputText = param.asStr();  // Get text input
  Serial.println("Sending to ATMEGA: " + inputText);  
  Serial1.println(inputText);  // Send to ATmega via UART
}

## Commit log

2025-04-11 cad files
    [LED Box.STL, Solenoid Holder.STL]
2025-05-01 pictures readme
    [LCD Box.STL]
